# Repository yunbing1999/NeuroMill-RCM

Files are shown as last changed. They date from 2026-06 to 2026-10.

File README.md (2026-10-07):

# NeuroMill Final

NeuroMill Final is a ROS 2 Jazzy workspace for teleoperating a UFACTORY xArm7
with a PS5 DualSense controller. It includes free Cartesian teleoperation,
fixed-tip control, two-level remote-center-of-motion (RCM) control, speed-limited
insertion and withdrawal, force/torque safety, haptic feedback, diagnostics,
and experiment logging.

The active ROS package is `neuro_final_teleop`.

> **Safety:** Develop and validate new motion features in UFACTORY Studio Sim
> first. Use low speed, keep the emergency stop accessible, and do not assume
> that a model-based RCM error is a physical measurement of the drill shaft.

## Current RCM Design

The RCM joint-velocity solver uses two priority levels:

```text
P1: maintain the captured RCM entry-point constraint
P2: operator rotation and insertion/withdrawal at equal priority
```

P2 is solved inside the null space of P1. Joint velocity and acceleration
limits are applied afterward. Insertion/withdrawal speed is limited, but cumulative
depth limits and depth-boundary slowdown are currently disabled.

The current controller assumes that the drill shaft is parallel to the modeled
tool `+Z` axis. This assumption has not yet been fully validated against the
physical drill mounting and remains an important limitation.

## Repository Layout

```text
NeuroMill_Final/
├── README.md
├── requirements.txt
├── rcm_logs/                       RCM experiment documentation and local CSVs
└── src/
    ├── neuro_final_teleop/         Main ROS 2 package
    └── external/                   xArm and ZED ROS packages
```

Important package files:

```text
src/neuro_final_teleop/
├── config/                         Runtime parameter profiles
├── experiments/                    SDK/KDL validation scripts
├── launch/                         ROS 2 launch files
├── neuro_final_teleop/
│   ├── neuro_final_teleop.py       Main node and parameters
│   ├── motion_modes.py             Operator commands and mode transitions
│   ├── force_haptics.py            FT safety and DualSense feedback
│   ├── control/
│   │   ├── kinematics.py           Calibrated PyKDL model
│   │   └── rcm_controller.py       Two-level RCM solver
│   └── nodes/
│       └── rcm_diagnostics_logger.py
└── test/                            Unit and dry-run tests
```

## Requirements

- Ubuntu 24.04
- ROS 2 Jazzy
- Python 3.12
- UFACTORY xArm Python SDK
- PyKDL
- PS5 DualSense controller
- Access to the xArm controller network

Optional components include the xArm force/torque sensor, RViz, and a ZED
camera with its SDK and ROS driver.

## First-Time Setup

```bash
cd ~
git clone git@github.com:yunbing1999/NeuroMill-RCM.git NeuroMill_Final
cd ~/NeuroMill_Final

source /opt/ros/jazzy/setup.bash

sudo apt update
sudo apt install -y \
  python3-colcon-common-extensions \
  python3-pip \
  python3-venv \
  python3-rosdep \
  python3-pykdl \
  ros-jazzy-robot-state-publisher \
  ros-jazzy-rviz2 \
  ros-jazzy-xacro

# Use a ROS-compatible Python environment. On Ubuntu 24.04, a venv avoids
# modifying the externally managed system Python installation.
python3 -m venv --system-site-packages ~/venvs/neuromill
source ~/venvs/neuromill/bin/activate
python3 -m pip install -r requirements.txt
rosdep update
rosdep install --from-paths src/neuro_final_teleop src/external/xarm_description --ignore-src -r -y

colcon build --packages-select xarm_description neuro_final_teleop
source install/setup.bash
```

Verify the package:

```bash
ros2 pkg prefix neuro_final_teleop
```

The command should return a path under this workspace's `install/` directory.

## Build After Code Changes

```bash
cd /home/yunbing/NeuroMill_Final
source /opt/ros/jazzy/setup.bash

colcon build \
  --symlink-install \
  --packages-select neuro_final_teleop

source install/setup.bash
```

Every new terminal must source both ROS and the workspace. If installed into the
venv above, activate it in each terminal as well (before building/running):

```bash
source /opt/ros/jazzy/setup.bash
source /home/yunbing/NeuroMill_Final/install/setup.bash
```

## Hardware Checklist

Before connecting the teleoperation node:

- Confirm whether Studio is in **Sim** or **Real** mode.
- Confirm that the intended robot is reachable at `192.168.1.243`.
- Confirm that no other program is commanding the robot.
- Connect the DualSense and check that pygame can see it.
- Verify the active TCP offset and payload in UFACTORY Studio.
- Keep motion speeds low for the first run.
- Keep the emergency stop accessible.

Check the controller:

```bash
ls -l /dev/input/js*

python3 -c 'import pygame; pygame.init(); pygame.joystick.init(); print([(i, pygame.joystick.Joystick(i).get_name()) for i in range(pygame.joystick.get_count())])'
```

If DualSense haptic output lacks permission, install an appropriate `udev`
rule for Sony VID `054c`, PID `0ce6`, then reconnect the controller.

## Calibrated Kinematics and TCP

The robot-specific joint-origin parameters are stored in:

```text
src/external/xarm_description/config/kinematics/user/
xarm7_kinematics_neuromill_check.yaml
```

They were exported from the xArm controller through
`gen_kinematics_params.py`, which reads 42 controller-resident values
(`7 joints × [x, y, z, roll, pitch, yaw]`) over TCP port 502.

At runtime teleop loads this YAML into the local `KDLKinModel`; the current
visualization launch also selects this calibration. Neither writes it back to
the controller:

```text
xArm controller calibration
        ↓ export
robot-specific kinematics YAML
        ↓ load at node startup
local KDL FK and Jacobian
        ↓
Tip-Lock and RCM solvers
```

The active UFACTORY controller TCP offset is read separately from
`arm.tcp_offset`. Its XYZ translation is applied to local KDL FK and the tool
Jacobian. TCP RPY is also applied to the modeled tool orientation and shaft axis.
No additional virtual-tip offset is supported.

Startup validation gates constrained modes using TCP position agreement between
SDK and KDL, and separately reports orientation error as a diagnostic. A small validation error proves numerical consistency between the two
models at that pose; it does not prove physical drill-tip or drill-axis
accuracy. TCP orientation and the physical shaft direction require separate
multi-pose and physical validation.

## Current RCM Experiment Startup

Stop duplicate nodes before starting. In every terminal:

```bash
cd /home/yunbing/NeuroMill_Final
source /opt/ros/jazzy/setup.bash
source install/setup.bash
```

If using the first-time setup venv, also activate ~/venvs/neuromill.
The following commands use the real robot configuration. They do not enable
simulation. Match the controller TCP and the display model:
XYZ = [-36.87, -7.58, 243.61] mm; RPY = [3.52, 2.74, 6.27] degrees.

Run each command in a separate sourced terminal, in this order:

1. Joint feedback:

   ```bash
   ros2 run neuro_final_teleop joint_state_bridge --ros-args -p robot_ip:=192.168.1.243
   ```

2. Calibrated robot, sensor, holder and approximate drill model:

   ```bash
   ros2 launch neuro_final_teleop rcm_sensor_view.launch.py mount_yaw_deg:=-78.382 shaft_length_m:=0.10 shaft_diameter_m:=0.005
   ```

3. RViz:

   ```bash
   rviz2 -d /home/yunbing/NeuroMill_Final/src/neuro_final_teleop/rviz/neuro_final.rviz
   ```

4. Force/torque bridge (auto-zero is enabled by default; start without contact):

   ```bash
   ros2 run neuro_final_teleop ft_bridge --ros-args -p robot_ip:=192.168.1.243 -p publish_hz:=100.0
   ```

5. RCM markers and summary:

   ```bash
   ros2 run neuro_final_teleop rcm_visualizer --ros-args -p max_trail_points:=15000
   ```

6. Basic logger, before capturing RCM:

   ```bash
   ros2 run neuro_final_teleop rcm_diagnostics_logger --ros-args -p log_mode:=basic -p output_dir:=/home/yunbing/NeuroMill_Final/rcm_logs/new_tcp/basic
   ```

7. Main teleop:

   ```bash
   ros2 run neuro_final_teleop neuro_final_teleop --ros-args \
     -r __node:=neuro_final_teleop \
     --params-file /home/yunbing/NeuroMill_Final/src/neuro_final_teleop/config/neuro_final_default.yaml \
     -p robot_ip:=192.168.1.243 \
     -p kinematics_yaml:=/home/yunbing/NeuroMill_Final/src/external/xarm_description/config/kinematics/user/xarm7_kinematics_neuromill_check.yaml \
     -p require_simulation_robot:=false \
     -p v7_speed_scale_default:=0.75 \
     -p v7_rcm_enable:=true \
     -p v7_rcm_insertion_enable:=true \
     -p v7_rcm_max_insertion_mm_s:=5.0 \
     -p v7_rcm_max_angular_deg_s:=2.0
   ```

8. Optional force-monitoring GUI:

   ```bash
   ros2 run neuro_final_teleop session_gui
   ```

Release the deadman and exit RCM before stopping teleop and the logger.
Each capture gets its own CSV/metadata pair. GUI rosbag recording is separate.

The drill mesh is approximate display geometry, not physical metrology.
The display TCP is a fixed calibration snapshot; changing the controller TCP
requires updating the visual model too. TF yellow arrows connect coordinate
origins, not physical parts; disable TF > Show Arrows to hide them.

## DualSense Controls

The current default deadman setting is `circle`; the input layer also accepts
R1 while this setting is active.

| Control | Free teleoperation | RCM mode |
|---|---|---|
| Hold Circle or R1 | Enable motion | Enable motion |
| Options | Capture and enter RCM | Exit RCM |
| Right stick | Cartesian orientation command | Tool-frame X/Y rotation |
| R2 | Positive/inward depth command | Insertion |
| L2 | Negative/outward depth command | Withdrawal |
| Cross | Enter Tip-Lock | No RCM action |
| R3 click | Toggle Tip-Lock when enabled | No RCM action |
| Square | FT tare | No mode change |
| Triangle | Orthogonal alignment | No mode change |
| L1 | Move to configured initial joint pose | Not handled until RCM is exited |
| D-pad up/down | Change speed scale | Change speed scale |
| D-pad left/right | J7 trim when allowed | — |
| Create | Recovery or quit, depending on state | Recovery or quit |

Important RCM behavior:

1. Move the tool tip to the intended entry point.
2. Press **Options** to capture that point and enter RCM.
3. Hold the deadman.
4. Use the right stick for constrained rotation.
5. Use R2/L2 for insertion/withdrawal when insertion is enabled.
6. Press **Options** again to exit RCM.

L1 uses `initial_pose_joint_deg_csv` unless
`initial_pose_use_startup:=true`. It is a joint-space target, not the RCM
capture pose.

## RCM Parameters

The RCM parameters are declared in `neuro_final_teleop.py`. Important defaults
are:

| Parameter | Default | Meaning |
|---|---:|---|
| `v7_rcm_enable` | `true` | Enable RCM mode |
| `v7_rcm_insertion_enable` | `false` | Allow L2/R2 motion in RCM |
| `v7_rcm_max_angular_deg_s` | `5.0` | Maximum operator rotation speed |
| `v7_rcm_max_insertion_mm_s` | `5.0` | Maximum insertion/withdrawal speed |
| `v7_rcm_correction_gain_s` | `12.0` | P1 error correction gain |
| `v7_rcm_max_correction_mm_s` | `10.0` | Maximum P1 correction speed |
| `v7_rcm_damping` | `0.025` | Damped pseudoinverse parameter |
| `v7_rcm_qdot_limit_rad_s` | `0.40` | Joint velocity limit |
| `v7_rcm_qddot_limit_rad_s2` | `1.50` | Joint acceleration limit |

Legacy depth-limit and travel-slowdown parameters remain declared, but the
current depth limiter passes commands through; do not rely on those parameters
to stop travel. Speed and joint limits remain active.

The characteristic length is currently calculated as:

```text
characteristic_length_m =
    (maximum insertion speed in m/s) / (maximum angular speed in rad/s)
```

Consequently, changing either maximum speed also changes the relative scaling
inside P2. This coupling is under evaluation and should be considered when
interpreting rotation-tracking results.

## Basic RCM Diagnostics

The main node publishes JSON diagnostics on:

```text
/neuro_final/rcm_diagnostics
```

Check one complete message:

```bash
ros2 topic echo \
  /neuro_final/rcm_diagnostics \
  std_msgs/msg/String \
  --once \
  --full-length
```

Start the basic logger before capturing RCM in a sourced terminal:

    ros2 run neuro_final_teleop rcm_diagnostics_logger --ros-args -p log_mode:=basic -p output_dir:=/home/yunbing/NeuroMill_Final/rcm_logs/new_tcp/basic

Each successful RCM capture creates a basic CSV and metadata JSON. Exiting RCM
closes the session; Ctrl+C closes any active file. See
[rcm_logs/README.md](rcm_logs/README.md) for the schema and data-source conventions.

The reported lateral RCM error is computed from encoder joint feedback and the
same calibrated KDL model used by the controller. It is useful for controller
and model consistency, but it is not an independent physical measurement. A
physical RCM-accuracy claim requires an external reference such as optical
tracking or a measured entry-point fixture.

## Other Runtime Components

| Executable | Purpose |
|---|---|
| `neuro_final_teleop` | Main teleoperation and RCM node |
| `ft_bridge` | Publish xArm force/torque data |
| `joint_state_bridge` | Publish `/joint_states` |
| `session_gui` | FT/haptic monitoring and rosbag recording |
| `rcm_diagnostics_logger` | Record capture-scoped basic RCM CSV data |
| `rcm_visualizer` | Publish captured entry coordinates, trajectory and error summary |

The generic teleop launch is below. It does not reproduce the calibrated RCM
experiment overrides above and does not start the RCM logger or visualizer:

```bash
ros2 launch neuro_final_teleop teleop.launch.py \
  robot_ip:=192.168.1.243
```

### Full RViz/ZED launch status

`system.launch.py` is not currently the recommended startup path. Its ZED
include block is commented out while the launch description still references
`zed_camera_launch`. Fix and test that launch file before using it for a formal
experiment.

## Dry Run

Dry run checks imports, parameters, and node construction without connecting
to the robot:

```bash
cd /home/yunbing/NeuroMill_Final
source /opt/ros/jazzy/setup.bash
source install/setup.bash

NEURO_FINAL_DRY_RUN=1 \
ros2 run neuro_final_teleop neuro_final_teleop --ros-args \
  -p enable_control_timer:=false
```

Dry run does not validate robot networking, physical motion, TCP calibration,
or DualSense hardware behavior.

## Development Checks

Run before committing controller changes:

```bash
cd /home/yunbing/NeuroMill_Final
source /opt/ros/jazzy/setup.bash
source install/setup.bash

python3 -m compileall -q \
  src/neuro_final_teleop/neuro_final_teleop

ROS_LOG_DIR=/tmp/neuro_rcm_test_logs \
python3 -m pytest -q \
  src/neuro_final_teleop/test/test_rcm_controller.py \
  src/neuro_final_teleop/test/test_rcm_kdl.py \
  src/neuro_final_teleop/test/test_rcm_node_dry_run.py \
  src/neuro_final_teleop/test/test_rcm_state_flow.py

colcon build \
  --symlink-install \
  --packages-select neuro_final_teleop
```

The full controller test file still contains historical depth-limit assertions
that conflict with the current unlimited-depth behavior. These tests need updating;
a full-suite pass is not currently claimed. The basic CSV and visualizer tests are
in test_basic_csv.py and test_rcm_visualizer.py.

## Known Limitations and Open Validation Work

- SDK-versus-KDL agreement proves model consistency, not absolute physical
  accuracy.
- Startup validation gates on TCP position; orientation error is diagnostic only.
- The solver currently assumes the physical shaft is aligned with tool `+Z`.
- The physical drill-axis offset must be measured and incorporated before
  claiming physical RCM accuracy.
- The characteristic length is coupled to the configured maximum insertion and
  rotation speeds.
- Combined rotation-and-insertion tests across a broad range of poses are still
  required.
- Real-robot tests must follow successful software and Studio Sim validation.
- `system.launch.py` requires repair before it can reliably launch the complete
  RViz/ZED stack.

## Git Workflow

Develop features on a branch rather than directly on `main`:

```bash
git switch main
git pull personal main
git switch -c <feature-branch>
```

Before pushing:

```bash
git diff --check
git status --short
```

Experiment outputs under rcm_logs/ are ignored by Git except rcm_logs/README.md.
Keep raw CSV and metadata pairs together locally.

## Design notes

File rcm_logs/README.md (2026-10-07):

# RCM Experiment Recordings

## Current directories

| Path | Contents |
|---|---|
| `new_tcp/basic/` | Basic recordings with the new TCP: 20 CSV files and 20 matching metadata JSON files, recorded on 2026-09-29, 2026-10-05, 2026-10-07 |
| `kinematics_validation/` | Kinematic validation: `sdk_kdl_fk_scan.csv` contains the earlier SDK/KDL comparison; `sdk_kdl_fk_scan_calibrated.csv` contains the calibrated KDL comparison |
| `archive/` | Earlier standard experiments, insertion demonstrations, and insertion pilot experiments; see the local `archive/README.md` for individual runs |

This inventory reflects local files as of 2026-10-07. Experiment data are not distributed with the repository; a fresh clone may not contain these directories or CSV files.

## Starting basic recording

Source the ROS 2 and workspace environments, then start the logger before entering RCM mode:

```bash
ros2 run neuro_final_teleop rcm_diagnostics_logger --ros-args \
  -p log_mode:=basic \
  -p output_dir:=/home/yunbing/NeuroMill_Final/rcm_logs/new_tcp/basic
```

Each successful RCM capture creates a CSV and a matching metadata JSON file. Exiting RCM closes the session; another capture creates new files. Ctrl+C closes any active recording.

## CSV fields

- `elapsed_s`: elapsed time since the first recorded sample, in seconds.
- `lateral_error_mm`: model-derived distance from the fixed entry point to the tool shaft axis, in millimetres.
- `tcp_x_mm`, `tcp_y_mm`, `tcp_z_mm`: model TCP position in the robot base frame, in millimetres.
- `q1_deg` through `q7_deg`: encoder feedback joint angles, in degrees.

The matching `_metadata.json` records the captured entry point, controller TCP, model configuration, units, and data sources. Keep it together with its CSV. Historical metadata preserves the configuration used at recording time and should not be rewritten to match the current code.

The current controller uses the configured physical TCP without an additional software virtual-tip offset. CSV RCM errors describe model consistency; independent optical measurements are needed to validate physical accuracy.

## File naming

`rcm_basic_20261005_151806_139375.csv` indicates the basic format, the date 2026-10-05, the time 15:18:06, and a microsecond component used to distinguish files. Its matching JSON shares the same timestamp.

## Git rules

Everything under `rcm_logs/` except this README is ignored by Git, including CSV files, metadata, plots, and archive documentation. Ignore rules do not delete local data.

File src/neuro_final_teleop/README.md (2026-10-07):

# neuro_final_teleop

Main ROS 2 Jazzy package for xArm7 DualSense teleoperation, fixed-tip and RCM
control, force feedback, basic CSV recording, and drill visualization.
See the [workspace README](../../README.md) for the current separate-terminal startup.

## Package map

| Path | Responsibility |
|---|---|
| neuro_final_teleop/neuro_final_teleop.py | Main node, parameters, controllers, diagnostics and capture events |
| neuro_final_teleop/motion_modes.py | Operator input, free/fixed-tip/RCM transitions and motion requests |
| neuro_final_teleop/force_haptics.py | Force processing, contact feedback and haptic output |
| neuro_final_teleop/control/ | KDL, solvers, state machine and protection helpers |
| neuro_final_teleop/input/ | DualSense backend and pygame fallback implementation |
| neuro_final_teleop/nodes/ | Independent bridge, GUI, logger and visualization nodes |
| neuro_final_teleop/drill_mesh.py | Continuous display-only drill mesh generation |
| neuro_final_teleop/assets/ | Controller-guide image |
| config/ | Default and alternative runtime parameter profiles |
| launch/ | Generic, visualization and playback launches |
| urdf/ | Calibrated robot/sensor/holder/drill display assembly |
| meshes/milling/ | Active static meshes |
| meshes/archive/ | Original reference meshes, not installed |
| rviz/ | RViz display configuration |
| experiments/ | SDK/KDL comparison tools; results go to rcm_logs/kinematics_validation |
| test/ | Unit and dry-run regression checks |

## Installed executable entry points

- neuro_final_teleop: main control node.
- ft_bridge: force/torque topic and tare service.
- joint_state_bridge: encoder feedback as joint states.
- session_gui: force monitoring, haptic controls and rosbag recording.
- rcm_diagnostics_logger: basic CSV and metadata per capture.
- rcm_visualizer: RCM entry coordinates, trajectory and summary markers.

## Current behavior

Controller TCP translation and rotation are used with the selected KDL model.
Software virtual-tip offsets and compact CSV output have been removed.
Insertion depth limits are disabled; insertion speed, joint velocity and
acceleration limits remain. Fixed-tip mode remains available.

Use rcm_sensor_view.launch.py for the current model. system.launch.py has an
unresolved ZED include reference and is not the recommended startup path.
Generic teleop.launch.py does not apply the full experiment overrides.
Playback uses ROS bags, not the basic CSV files.

Some historical depth-limit tests still require updates. Display geometry and
model-derived errors are not independent physical accuracy measurements.

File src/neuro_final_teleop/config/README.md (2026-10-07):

# Config

This folder contains the runtime YAML profiles for the `neuro_final_teleop` node.

```text
neuro_final_default.yaml   Normal operation values.
neuro_final_safe.yaml      Slower safety-focused values.
neuro_final_drilling.yaml  Drilling-practice values.
```

Each file is keyed by the ROS node name:

```yaml
neuro_final_teleop:
  ros__parameters:
    ...
```

The main node already uses the matching name neuro_final_teleop. The explicit
remap below is optional; if you choose a different node name, update the YAML key:

```bash
ros2 run neuro_final_teleop neuro_final_teleop --ros-args \
  -r __node:=neuro_final_teleop \
  --params-file src/neuro_final_teleop/config/neuro_final_default.yaml
```

Use launch arguments, such as `robot_ip:=...`, for machine-specific values instead of editing the YAML for every computer.

The current workflow uses neuro_final_default.yaml with explicit calibrated-KDL
and RCM speed overrides from the workspace README. Default stick signs are
lx=-1, ly=+1, rx=-1, ry=-1. Alternative profiles are not automatically merged,
and the safe profile name does not guarantee lower values for every parameter.
Virtual-tip parameters are no longer supported.

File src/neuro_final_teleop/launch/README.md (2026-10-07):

# Launch files

| File | Current purpose/status |
|---|---|
| teleop.launch.py | Generic FT bridge, joint bridge, teleop and GUI; not the full calibrated RCM experiment configuration |
| bridge_only.launch.py | FT and joint-state bridges only |
| rcm_sensor_view.launch.py | Current calibrated robot/sensor/holder/drill display via robot_state_publisher; no robot motion commands |
| playback.launch.py | Robot/ZED visualization, RViz and GUI using simulated ROS time; use with ros2 bag play --clock |
| system.launch.py | Legacy combined workflow; currently broken because zed_camera_launch is referenced while its definition is commented out |

Use the [workspace README](../../../README.md) for the complete current startup.
Do not run overlapping generic launches alongside the separate-terminal nodes.

## Model parameters

rcm_sensor_view.launch.py defaults: sensor_height_m=0.056,
sensor_diameter_m=0.072, mount_yaw_deg=-78.382, shaft_length_m=0.10,
shaft_diameter_m=0.005. It selects neuromill_check kinematics, generates a temporary
continuous drill mesh and loads the display xacro.

Mount yaw and drill shape are approximate display geometry. TCP is a fixed
snapshot in the xacro and is not automatically read from the controller.

Playback still requires ZED description assets and does not replay basic CSV.
The generic teleop/system definitions expose debug_topic_enable, trigger_enable
and rumble_enable arguments; this does not resolve the system launch error.

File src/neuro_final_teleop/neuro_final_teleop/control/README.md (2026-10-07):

# control

Reusable control and safety modules for NeuroFinal teleoperation.

`base_node.py`

Common ROS node setup: parameters, xArm SDK connection, health checks, state transitions, velocity sending, tare action, alignment action, and shutdown.

`fixed_point_ik.py`

Joint-space fixed-point solver used by fixed-tip mode.

`ft_guard.py`

Force/torque guard that evaluates fresh/stale data, hard limits, warning slowdown, and inward-motion blocking.

`kinematics.py`

PyKDL xArm7 model used for forward kinematics, Jacobian calculations, and SDK/model validation.

`math_utils.py`

Small math helpers used by motion and safety code.

`tip_lock_controller.py`

Fixed-tip controller helper used by the active X/R3 constrained mode.

`safety.py`

Rate limiting, joint-risk checks, and safety helper classes.

`state_machine.py`

Explicit teleop state machine with allowed transitions for idle, free teleop, fixed-tip capture/active states, alignment, and fault recovery.

## RCM controller and current limits

rcm_controller.py implements captured entry-point geometry and a two-level
joint-velocity solver: lateral RCM correction first, operator rotation/insertion
second. Cumulative depth limits and boundary slowdown are disabled; speed and
joint acceleration/velocity limits remain active.

kinematics.py applies controller TCP translation and RPY rotation with the
selected KDL model. No software virtual-tip offset is added. Position validation
gates constrained modes; orientation mismatch is reported diagnostically.

The state machine includes RCM capture/active states. Fixed-tip functionality is
separate from RCM and remains supported. Historical depth-limit assertions in
test_rcm_controller.py still need updating to match the current behavior.

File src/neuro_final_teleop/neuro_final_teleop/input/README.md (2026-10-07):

# input

Input backends for NeuroFinal teleoperation.

`dualsense.py`

Primary input path. It reads a PS5 DualSense controller through `dualsense-controller`, maps PS5 buttons into the teleop input snapshot, and sends vibration/adaptive-trigger feedback when the `hidraw` device is writable.

Default PS5 mapping:

```text
Circle/R1    Deadman hold
Options      RCM capture/exit
Cross        Fixed-tip capture/release
Square       Force/torque tare
Triangle     Orthogonal alignment
L1           Initial pose action
Create       Fault recovery or quit
Left stick   Base-frame planar motion
R3 + right stick Fixed-tip entry/control
L2/R2        Depth out/in
D-pad up/down Speed scale
D-pad left/right J7 trim when sticks are idle
```

`gamepad.py`

Fallback pygame/SDL input layer for generic gamepads. The main NeuroFinal node uses the DualSense layer for normal operation.

In RCM mode the right stick commands constrained rotation and L2/R2 command
withdrawal/insertion when enabled. Mode handling is in motion_modes.py, not
only the input backend. Default YAML signs are lx=-1, ly=+1, rx=-1, ry=-1.

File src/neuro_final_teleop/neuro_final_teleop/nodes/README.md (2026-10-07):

# nodes

Independent ROS nodes used by the live and recording workflows.

`ft_bridge.py`

Connects to the xArm SDK, initializes the force/torque sensor, publishes `/xarm/ft_data`, and provides `/xarm/tare_sensor`.

`joint_state_bridge.py`

Connects to the xArm SDK and publishes `/joint_states` for robot visualization and recording.

`session_gui.py`

PyQt GUI for live force/torque monitoring, haptic evaluation controls, tare command, and rosbag recording.

The GUI recorder writes sessions under `~/NeuroFinal/recordings` unless `NEURO_FINAL_RECORDING_ROOT` is set.

## RCM recording and visualization

rcm_diagnostics_logger.py supports only basic output (log_mode:=basic remains
accepted). Start before capture: /neuro_final/rcm_log_event opens/closes sessions,
and /neuro_final/rcm_diagnostics supplies samples. Each session produces CSV and
metadata JSON. See the workspace rcm_logs/README.md for fields.

rcm_visualizer.py publishes /neuro_final/rcm_markers in link_base, converting
millimetres to metres. It shows the captured entry XYZ, TCP, trajectory and error
statistics. On pause/exit it retains the last snapshot while the node runs.
The displayed drill geometry is separately supplied by RobotModel.

ft_bridge auto-zero is enabled by default. The GUI displays bridge data; main
teleop implements controller haptics. GUI rosbag recording is independent of
the basic CSV logger.

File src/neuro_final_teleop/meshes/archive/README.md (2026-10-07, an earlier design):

# Archived source meshes

These original CAD-export meshes are retained for reference and future remodeling:

- `Mount_Milling_xArm.stl`: original holder mesh.
- `Model_Milling.stl`: simplified tool mesh, not a full EMAX2PLUS model.
- `Mount_and_Milling.stl`: combined holder and simplified tool mesh.

No active source code or launch file references these STL files. They retain their
original coordinates and scale and are not installed by setup.py.

Current RViz geometry uses `../milling/mount_sensor_frame_m.stl` and the continuous
drill mesh generated by `drill_mesh.py`, with `../milling/drill_continuous_m.stl`
as the default static mesh. Do not substitute archived meshes without checking
units and transforms.

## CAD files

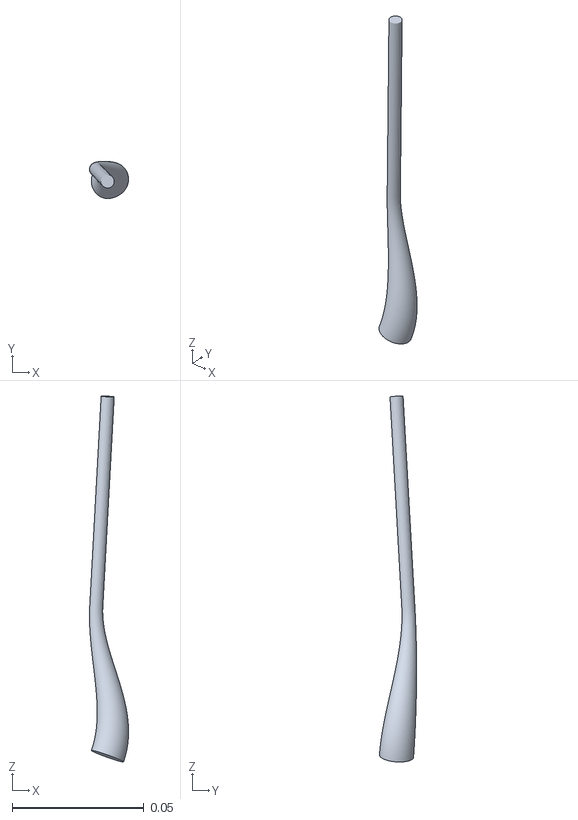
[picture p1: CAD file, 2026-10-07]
src/neuro_final_teleop/meshes/milling/drill_continuous_m.stl
0.0149 x 0.0141 x 0.139

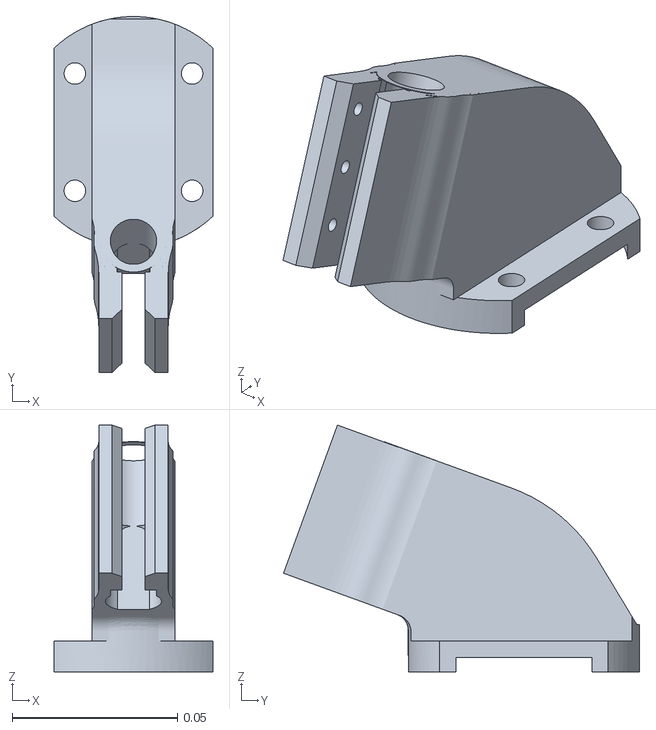
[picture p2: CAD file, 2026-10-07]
src/neuro_final_teleop/meshes/milling/mount_sensor_frame_m.stl
0.048 x 0.108 x 0.0747

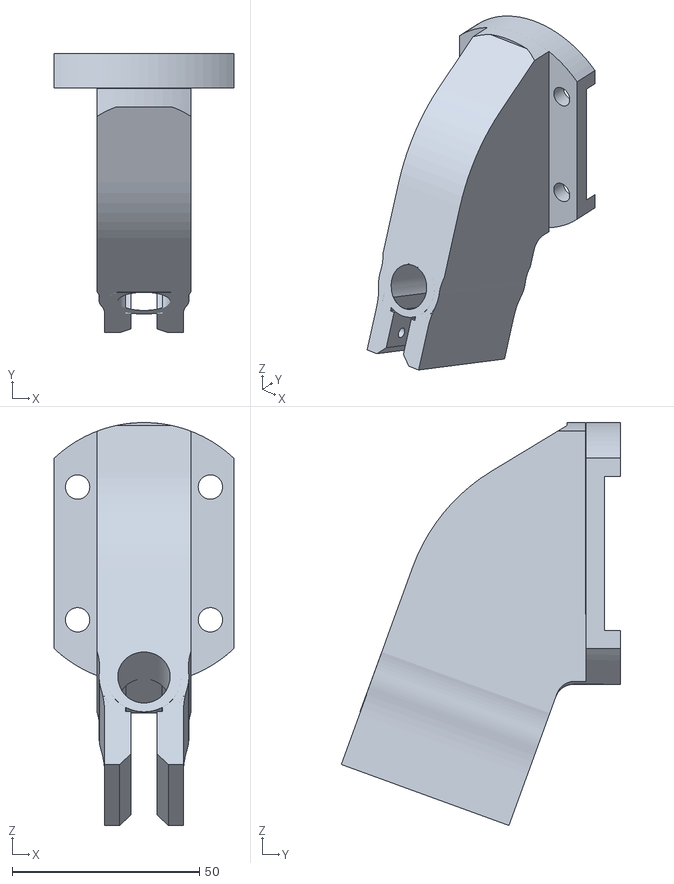
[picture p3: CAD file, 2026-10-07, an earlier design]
src/neuro_final_teleop/meshes/archive/Mount_Milling_xArm.stl
48.0 x 74.7 x 107.7

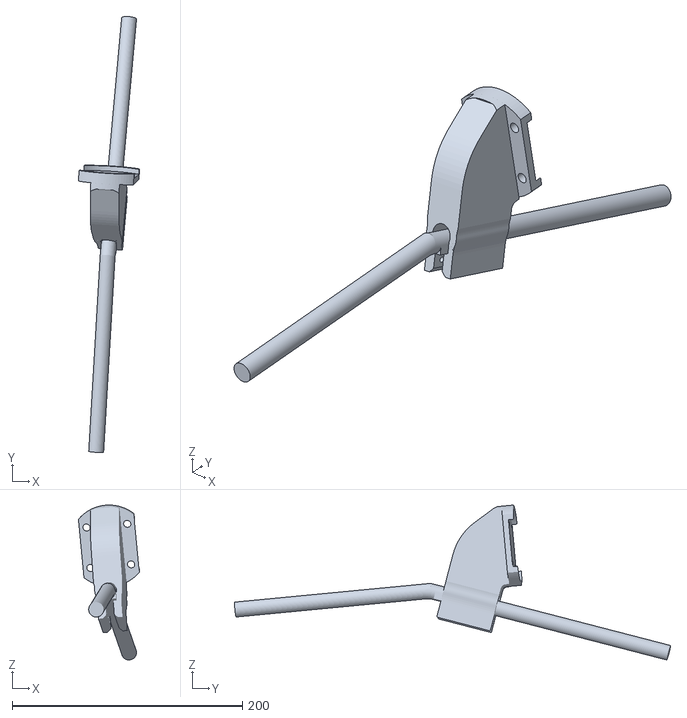
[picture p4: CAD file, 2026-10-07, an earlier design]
src/neuro_final_teleop/meshes/archive/Mount_and_Milling.stl
53.1 x 378.3 x 134.4

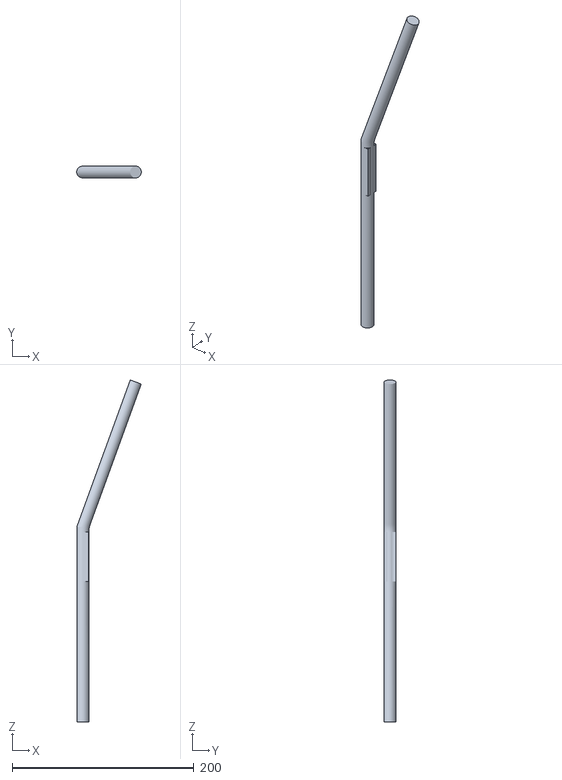
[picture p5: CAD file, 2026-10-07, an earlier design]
src/neuro_final_teleop/meshes/archive/Model_Milling.stl
71.2 x 13.0 x 376.6

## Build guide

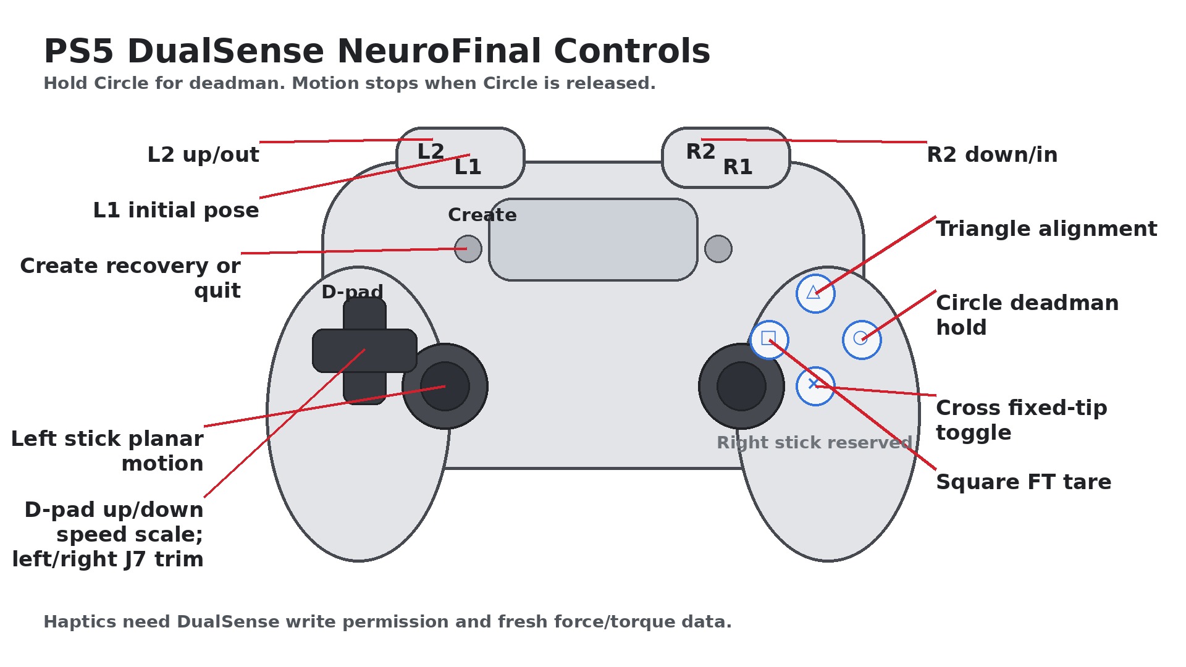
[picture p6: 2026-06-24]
src/neuro_final_teleop/neuro_final_teleop/assets/ps5_controller_guide.jpg

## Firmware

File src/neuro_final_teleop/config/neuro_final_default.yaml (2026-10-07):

neuro_final_teleop:
  ros__parameters:
    robot_ip: "192.168.1.243"
    dry_run: false
    loop_hz: 120.0
    velocity_watchdog_s: 0.0
    input_filter_alpha: 0.85
    input_release_alpha: 1.0
    # Joystick direction: +1 keeps input direction; -1 reverses it.
    lx_sign: -1.0
    ly_sign: 1.0
    rx_sign: -1.0
    ry_sign: -1.0
    v7_deadman_button: circle
    v7_speed_scale_default: 0.75
    v7_speed_scale_min: 0.15
    v7_speed_scale_max: 1.0
    v7_speed_scale_step: 0.05
    initial_pose_use_startup: false
    initial_pose_joint_deg_csv: "0,-40,0,75,0,115.1,1.5"
    tip_lock_max_angular_deg_s: 6.0
    v7_tip_lock_r3_toggle_enable: true
    v7_tip_lock_right_stick_control: true
    v7_tip_lock_tool_frame_control: true
    v7_tip_lock_pose_source: sdk_tcp
    v7_tip_lock_tcp_rotation_comp_enable: false
    v7_tip_lock_max_linear_mm_s: 14.0
    v7_tip_lock_correction_gain: 14.0
    v7_tip_lock_correction_deadband_mm: 0.02
    v7_tip_lock_recovery_err_mm: 0.45
    v7_tip_lock_recovery_gain_mm_s_per_mm: 3.0
    v7_tip_lock_min_angular_scale: 0.0
    v7_tip_lock_error_brake_enable: true
    v7_tip_lock_error_brake_mm: 0.30
    v7_tip_lock_error_brake_exp: 2.5
    v7_tip_lock_joint_ik_enable: true
    v7_tip_lock_joint_ik_pos_gain_s: 14.0
    v7_tip_lock_joint_ik_max_correction_mm_s: 12.0
    v7_tip_lock_joint_ik_damping: 0.025
    v7_tip_lock_joint_ik_qdot_limit_rad_s: 0.45
    v7_tip_lock_joint_ik_qddot_limit_rad_s2: 1.8
    v7_tip_lock_joint_ik_nullspace_gain: 0.05
    v7_tip_lock_joint_ik_hold_wz: true
    max_linear_mm_s: 20.0
    max_depth_mm_s: 4.0
    v7_force_watchdog_zero: true
    v7_use_tool_z_depth_in_free: false
    v7_use_tool_z_depth_in_tip_lock: true
    insertion_along_neg_tool_z: false
    v7_depth_planar_deadband: 0.17
    v7_ft_global_stop_enable: true
    v7_ft_global_soft_slowdown: true
    v7_ft_global_soft_min_scale: 0.15
    v7_ft_allow_retreat_on_limit: true
    v7_ft_retreat_speed_scale: 0.45
    v7_ft_retreat_min_cos: 0.10
    v7_contact_error_auto_recover: true
    v7_contact_error_code: 31
    v7_contact_recovery_cooldown_s: 0.70
    v7_vc_reject_soft_codes: [1]
    ft_fx_limit_n: 15.0
    ft_fy_limit_n: 15.0
    ft_fz_limit_n: 15.0
    ft_tx_limit_nm: 8.0
    ft_ty_limit_nm: 8.0
    ft_tz_limit_nm: 5.0
    ft_force_norm_limit_n: 15.0
    ft_torque_norm_limit_nm: 10.0
    ft_warning_ratio: 0.85
    v7_ft_haptic_enable: true
    v7_haptics_boot_test: false
    v7_ft_haptic_force_source: norm
    # Depth-input gating is OFF by default: contact feedback should appear as
    # soon as the tool/needle touches the object, regardless of whether the
    # operator is currently holding the trigger.
    v7_ft_haptic_require_depth_input: false
    v7_ft_haptic_depth_input_min: 0.05
    v7_haptic_feedback_gain: 1.12
    # Default event-pulse minimum was 160 ms; allow shorter taps so the
    # first-contact acknowledgement can be ~50 ms instead of 160 ms.
    v7_haptic_event_min_duration_ms: 40
    # No "starting floor" for proportional output: contact begins from zero
    # and grows with the force shift, so vibration ramps low->high.
    v7_contact_min_haptic_ratio: 0.03
    # Proportional full-scale: force at which the adaptive trigger reaches
    # maximum continuous-resistance (force=255). Sized so the operator gets
    # a wide "keep pressing -> keep getting harder" range before saturation,
    # instead of slamming into the lock at the first real touch.
    # The 15 N hardware safety stop is still enforced by _apply_global_ft_guard.
    v7_ft_haptic_full_scale_n: 13.0
    v7_ft_haptic_full_scale_torque_nm: 7.0
    v7_ft_haptic_include_torque: false
    v7_ft_haptic_warn_ratio: 0.0
    v7_ft_haptic_release_ratio: 0.0
    v7_ft_haptic_force_alpha: 0.48
    # Shift gate is the new deadband, so the legacy scalar deadband can be small.
    v7_ft_haptic_deadband_n: 0.05
    v7_ft_haptic_torque_deadband_nm: 0.51
    # Linear force->ratio curve so the operator feels a clean low->high climb
    # across the whole 0.25 N (touch) ... 5 N (locked) working range.
    v7_ft_haptic_shape_exp: 0.75
    # Slightly slower attack than the previous 0.85 floor so the proportional
    # ramp is a perceptible "growing" instead of a 1-frame snap to target.
    # 0.65 reaches ~96% of target in ~25 ms at 120 Hz -- fast but still felt.
    v7_ft_haptic_smooth_alpha: 0.75
    # Hard-block lock-up is OFF. It used to switch the DualSense trigger from
    # continuous_resistance to hard_resistance/section_resistance whenever
    # raw_ratio reached 1.0 -- and that effect switch is exactly what the
    # operator perceives as the trigger "releasing" at high force. Letting
    # the proportional path saturate at continuous_resistance(force=255) is
    # mechanically the same lock-up, but smooth (no effect switch, no release).
    v7_ft_haptic_hard_block_enable: false
    v7_ft_haptic_contact_on_ratio: 0.0
    v7_ft_haptic_contact_off_ratio: 0.002
    v7_ft_haptic_contact_on_dwell_s: 0.03
    v7_ft_haptic_contact_off_dwell_s: 0.08
    v7_ft_haptic_min_contact_feedback: 0.06
    v7_ft_haptic_max_trigger_resistance: 1.0
    v7_ft_haptic_trigger_start_position: 0
    v7_ft_haptic_trigger_end_position: 9
    v7_ft_haptic_trigger_preload_strength: 1
    v7_ft_haptic_trigger_max_strength: 8
    v7_ft_haptic_progressive_trigger_enable: false
    v7_ft_haptic_auto_tare_enable: true
    v7_ft_hardware_tare_enable: false
    # --- Per-channel enable flags so trigger-only vs vibration-only vs both
    # can be A/B compared during the needle-injection study.
    v7_ft_haptic_trigger_enable: true
    v7_ft_haptic_rumble_enable: true
    v7_ft_haptic_rumble_continuous_enable: false
    v7_haptic_event_gain: 0.0

    # First-contact tactile acknowledgement: one short rumble pulse on the
    # rising edge of contact_active, before the proportional loop starts.
    # Tuned to be a brief tap, not a startle.
    v7_ft_haptic_contact_pulse_enable: true
    v7_ft_haptic_contact_pulse_strength: 0.35
    v7_ft_haptic_contact_pulse_duration_ms: 50
    v7_ft_haptic_rumble_interval_s: 0.04
    v7_ft_haptic_vibration_min_ratio: 0.0
    # Vibration must ramp low->high. min_strength=0 ensures we are truly silent
    # just after contact, and shape_exp>1 compresses the low-force end so a
    # light touch barely buzzes while a firm press still drives the rumble up.
    v7_ft_haptic_rumble_min_strength: 0.0
    v7_ft_haptic_rumble_max_strength: 0.65
    v7_ft_haptic_rumble_shape_exp: 1.8
    v7_ft_haptic_rumble_min_interval_s: 0.06
    v7_ft_haptic_rumble_max_interval_s: 0.50
    v7_ft_haptic_rumble_min_duration_ms: 28
    v7_ft_haptic_rumble_max_duration_ms: 90
    v7_ft_haptic_release_pulse_enable: false
    v7_ft_haptic_trigger_vibration_enable: false
    v7_ft_haptic_debug: false
    v7_ft_haptic_debug_interval_s: 0.25
    # --- Shift-from-baseline contact detection: the primary contact gate.
    # The absolute v7_contact_on/off thresholds remain as a secondary defence
    # but are not OR'd with the shift gate when this is true.
    v7_contact_shift_gate_enable: true
    # Tuned to sit above realistic xArm motion noise: when the arm
    # accelerates/decelerates with a tool mounted, the FT sensor sees inertial
    # bumps in the 0.10-0.20 N range. A 0.25 N threshold rejects those while
    # still firing on a real ~0.3 N+ touch.
    v7_contact_shift_threshold_n: 0.76  
    v7_contact_shift_off_threshold_n: 0.38
    # Dwell long enough that brief motion transients (<100 ms) cannot satisfy
    # it, but short enough that a real touch is still felt as immediate.
    # This is the only contact-onset delay (the secondary on_dwell is bypassed
    # in node.py whenever the shift gate is enabled).
    v7_contact_shift_dwell_s: 0.05
    v7_contact_baseline_alpha: 0.003
    v7_ft_global_include_torque: false
    v7_motion_haptic_enable: false

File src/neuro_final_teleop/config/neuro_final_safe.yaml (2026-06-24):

neuro_final_teleop:
  ros__parameters:
    robot_ip: "192.168.1.243"
    dry_run: false
    loop_hz: 100.0
    velocity_watchdog_s: 0.0
    max_linear_mm_s: 12.0
    max_depth_mm_s: 2.5
    tip_lock_max_angular_deg_s: 8.0
    v7_tip_lock_r3_toggle_enable: true
    v7_tip_lock_right_stick_control: true
    v7_tip_lock_tool_frame_control: true
    v7_use_tool_z_depth_in_free: false
    v7_use_tool_z_depth_in_tip_lock: true
    insertion_along_neg_tool_z: false
    v7_tip_lock_joint_ik_hold_wz: true
    v7_force_watchdog_zero: true
    v7_ft_global_stop_enable: true
    v7_ft_global_soft_slowdown: true
    v7_ft_allow_retreat_on_limit: true
    v7_ft_retreat_speed_scale: 0.35
    v7_ft_retreat_min_cos: 0.10
    ft_fx_limit_n: 20.0
    ft_fy_limit_n: 20.0
    ft_fz_limit_n: 20.0
    ft_force_norm_limit_n: 60.0
    ft_torque_norm_limit_nm: 2.0
    v7_ft_haptic_enable: true
    v7_ft_haptic_full_scale_n: 50.0
    v7_ft_haptic_max_trigger_resistance: 0.55
    v7_motion_haptic_enable: false

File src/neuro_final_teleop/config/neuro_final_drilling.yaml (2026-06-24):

neuro_final_teleop:
  ros__parameters:
    robot_ip: "192.168.1.243"
    dry_run: false
    loop_hz: 140.0
    velocity_watchdog_s: 0.0
    max_linear_mm_s: 18.0
    max_depth_mm_s: 4.0
    tip_lock_max_angular_deg_s: 10.0
    v7_tip_lock_r3_toggle_enable: true
    v7_tip_lock_right_stick_control: true
    v7_tip_lock_tool_frame_control: true
    v7_force_watchdog_zero: true
    v7_use_tool_z_depth_in_free: false
    v7_use_tool_z_depth_in_tip_lock: true
    insertion_along_neg_tool_z: false
    v7_tip_lock_joint_ik_hold_wz: true
    v7_ft_global_stop_enable: true
    v7_ft_global_soft_slowdown: true
    v7_ft_allow_retreat_on_limit: true
    v7_ft_retreat_speed_scale: 0.45
    v7_ft_retreat_min_cos: 0.08
    ft_fx_limit_n: 80.0
    ft_fy_limit_n: 80.0
    ft_fz_limit_n: 80.0
    ft_force_norm_limit_n: 80.0
    ft_warning_ratio: 0.90
    v7_ft_haptic_enable: true
    v7_ft_haptic_force_source: norm
    v7_ft_haptic_full_scale_n: 70.0
    v7_ft_haptic_force_alpha: 0.08
    v7_ft_haptic_deadband_n: 0.8
    v7_ft_haptic_shape_exp: 0.70
    v7_ft_haptic_smooth_alpha: 0.45
    v7_ft_haptic_hard_block_enable: false
    v7_ft_haptic_max_trigger_resistance: 0.85
    v7_ft_haptic_rumble_enable: true
    v7_ft_haptic_rumble_continuous_enable: false
    v7_ft_haptic_contact_pulse_enable: true
    v7_ft_haptic_contact_pulse_strength: 0.30
    v7_ft_haptic_contact_pulse_duration_ms: 45
    v7_ft_haptic_vibration_min_ratio: 0.02
    v7_ft_haptic_rumble_min_strength: 0.18
    v7_ft_haptic_rumble_max_strength: 1.0
    v7_ft_haptic_rumble_shape_exp: 0.55
    v7_ft_haptic_rumble_min_interval_s: 0.04
    v7_ft_haptic_rumble_max_interval_s: 0.65
    v7_ft_haptic_rumble_min_duration_ms: 25
    v7_ft_haptic_rumble_max_duration_ms: 85
    v7_contact_shift_gate_enable: true
    v7_contact_shift_threshold_n: 0.76
    v7_contact_shift_off_threshold_n: 0.38
    v7_contact_shift_dwell_s: 0.05
    v7_contact_baseline_alpha: 0.003
    v7_motion_haptic_enable: false
